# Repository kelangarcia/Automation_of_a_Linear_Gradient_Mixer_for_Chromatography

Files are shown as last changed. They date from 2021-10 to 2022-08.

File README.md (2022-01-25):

# Automation-of-a-Linear-Gradient-Mixer-for-Chromatography

This repository has all the files and documentation (3D Case, Code, Circuit Analysis, Circuit Simulations, Procedure, Schematics,Results etc.) that were used to create a machine that automates the process of mixing gradients for chromatography. A so called Gradient Mixer Machine.

All the folders and files included are explained below:

- "Automation of Gradient Mixer for Chromatography.pdf": Technical motivation and explanation of the machine. Includes explanation of the final design, circuit, code, etc... works.

- "3D Case": This folder includes the 3D files exported into .stl (This is the format used for 3D printing). Just upload this file to a 3D printer or sent it to a production company.

- "Circuit": It includes the "Circuit_Diagram.pdf" file, this is supporting material for when you are soldering the components. It is a good guide. It also includes the Datasheets for the most important hardware components used. Like the solenoid valve, and transistor.

- "Code": This folder includes three important files. Two gradient mixer codes and a zip file with the needed libraries. The zip file needs to be installed into your Arduino IDE (read the instruction set for more), once it is installed. You can upload one of the two Gradient Mixer code provided. First try with the original code and test the machine. If you notice that when there is a press in the touch screen it detects the touch but in the inverted y-axis position, then upload the second code (LCD inverted code).

- "Instruction Sets": Two .pdf files, one is the instructions for the user, and the other has the instructions for making the gradient mixer.

- "PCB": Includes the .fzz file for editing the PCB design, and it also includes the export files of the pcb in three diferent formats (.pdf, .svg, Gerber Files). Depending on the company you are printing the PCB with, they will request for the type of file. The most common is the Gerber File. The file "KGGradient_Mixer_06072021.zip" has all the Gerber Files compressed into a zip folder, you can send this zip file to the production company, or create your own zip file with the provided Gerber files.
 
- "EXTRA": Extra material

- "Gradient Mixer Price": List of materials with their average price inthe market, giving how much does this gradient mixer construction cost.

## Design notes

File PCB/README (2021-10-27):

Printing PCB

The export files of the PCB are in the folder "Production_Files". In there, all files are given in the most important formats.
In .pdf, .svg, and gerber file (the most important).
For PCB production, normaly gerber files are used. Just download all the gerber files, zip them together to one file and send it to the production company.
(Or just send the .zip file included with the name "KGGradient_Mixer_06072021.zip" which is located on the folder "Production File", which is a zip file containing the gerber files)

If you want to modify the PCB design, the file is also included with the name "Gradient_Mixer_05.07.2021.fzz" to edit this file you need the software fritzing.

When the pcb is ready, you need to solder all the components into the PCB, the circuit diagram showing which components to solder exactly where is on the pdf with the name
"Circuit_Diagram.pdf" on the folder name "Circuit"

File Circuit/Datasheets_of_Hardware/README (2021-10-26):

Datasheets of the transistor used (NPN TIP 120 Darlington Transistor) and the Solenoid valve used (Delays where taken into consideration).

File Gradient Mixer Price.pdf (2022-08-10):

Utility | Component | Price
Materials | 3.2" TFT LCD Display Touchscreen | € 15.24
| 3.2" TFT LCD Mega Shield V2.2 | € 12.39
| Arduino Mega 2560 | € 35.00
| TIP 120 Darlington Transistor | € 0.30
| 1N4001 Diodes 1A 50V | € 1.29
| Led's, Resistors, Interrupt Buttons,
| pins | € 7.99
| Long Arduino Pins | € 1.00
| 433MHz Wireless
| Transmitter/Receiver | € 1.90
| 433Mhz Wireless Power Socket | € 17.90
| 12V Power Supply | € 10.99
| Connectors | € 11.75
| 22AWG Electric Wire | € 8.99
| 1.5mm screws | € 1.00
| Printed 3D case | € 37.00
| Printed Circuit Board | € 34.00
| Solenoid Valve | € 150.00
| GPIO Cable 40 Pin Male to Female | € 21.00
| Extra High Female Pin Headers | € 10.00
| SubTotal | € 377.74
Equipment | Solder | € 10.00
| Tin | € 5.00
| Multimeter | € 5.00
| SubTotal | € 20.00
| Total | € 397.74

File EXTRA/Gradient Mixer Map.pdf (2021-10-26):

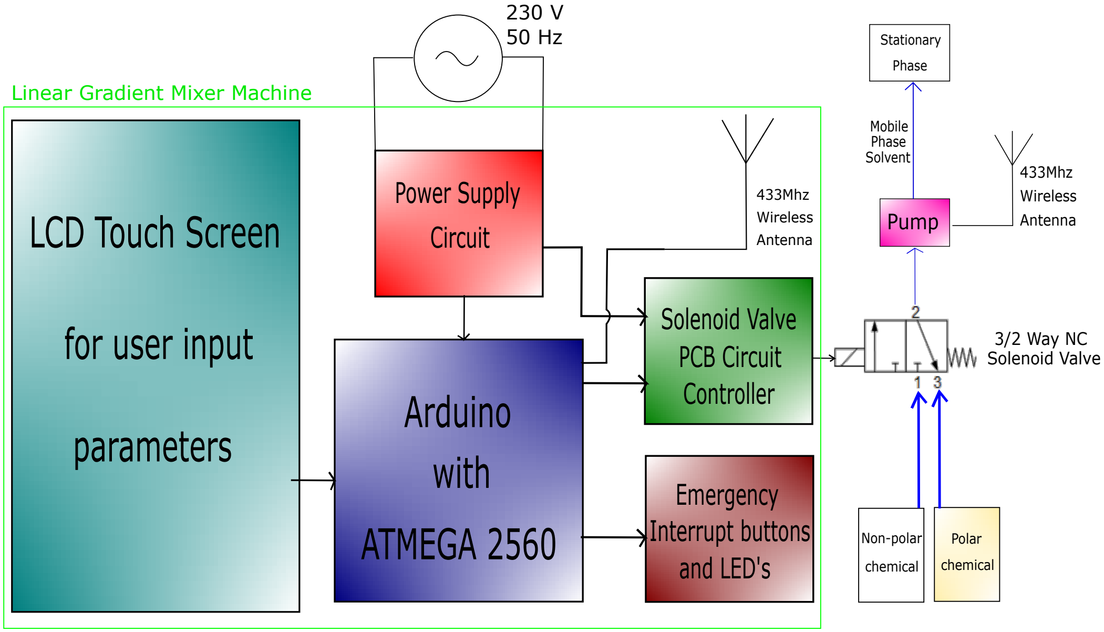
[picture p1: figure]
Arduino with ATMEGA 2560; PCB Circuit; Solenoid Valve; Emergency Interrupt buttons and LED's; LCD Touch Screen; for user input; Power Supply Circuit; parameters; 433Mhz Wireless Antenna; 3/2 Way NC Solenoid Valve; Non-polar; chemical; Polar; 433Mhz Wireless; Pump; Antenna; Mobile Phase Solvent; Stationary; Phase; Linear Gradient Mixer Machine; Controller

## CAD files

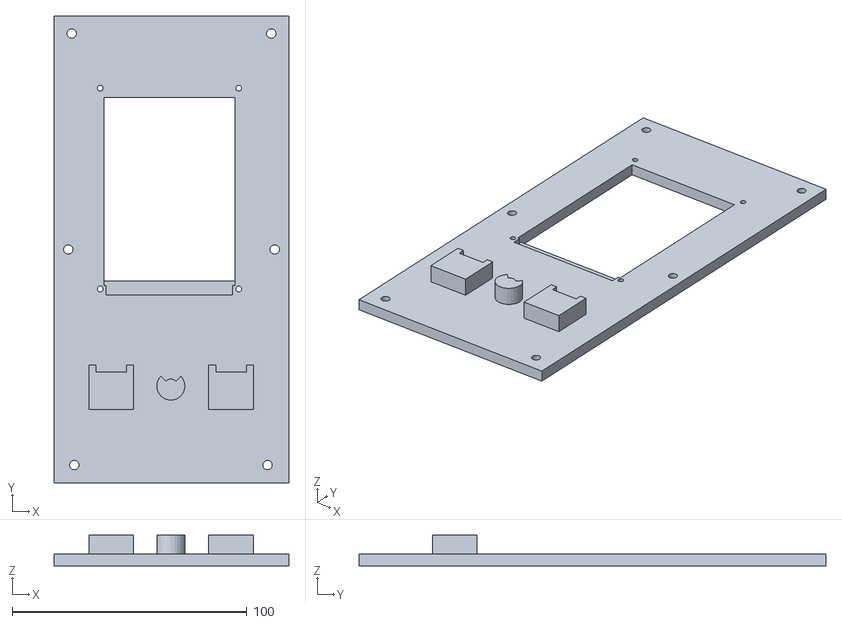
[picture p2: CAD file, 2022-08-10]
3D Case/Lid.stl
100.0 x 199.0 x 13.0

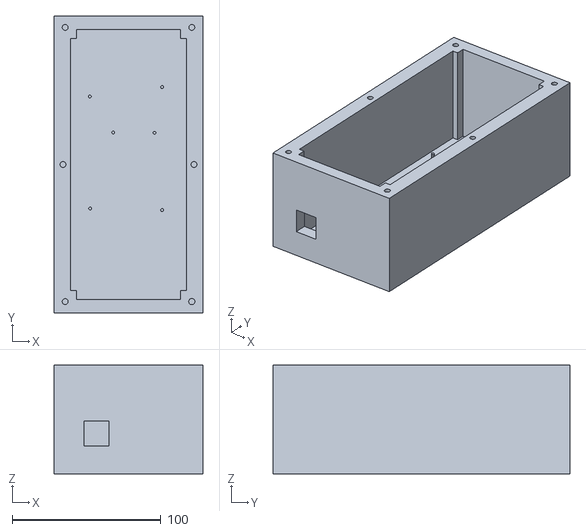
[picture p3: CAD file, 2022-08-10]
3D Case/Base.stl
100.0 x 199.0 x 73.0

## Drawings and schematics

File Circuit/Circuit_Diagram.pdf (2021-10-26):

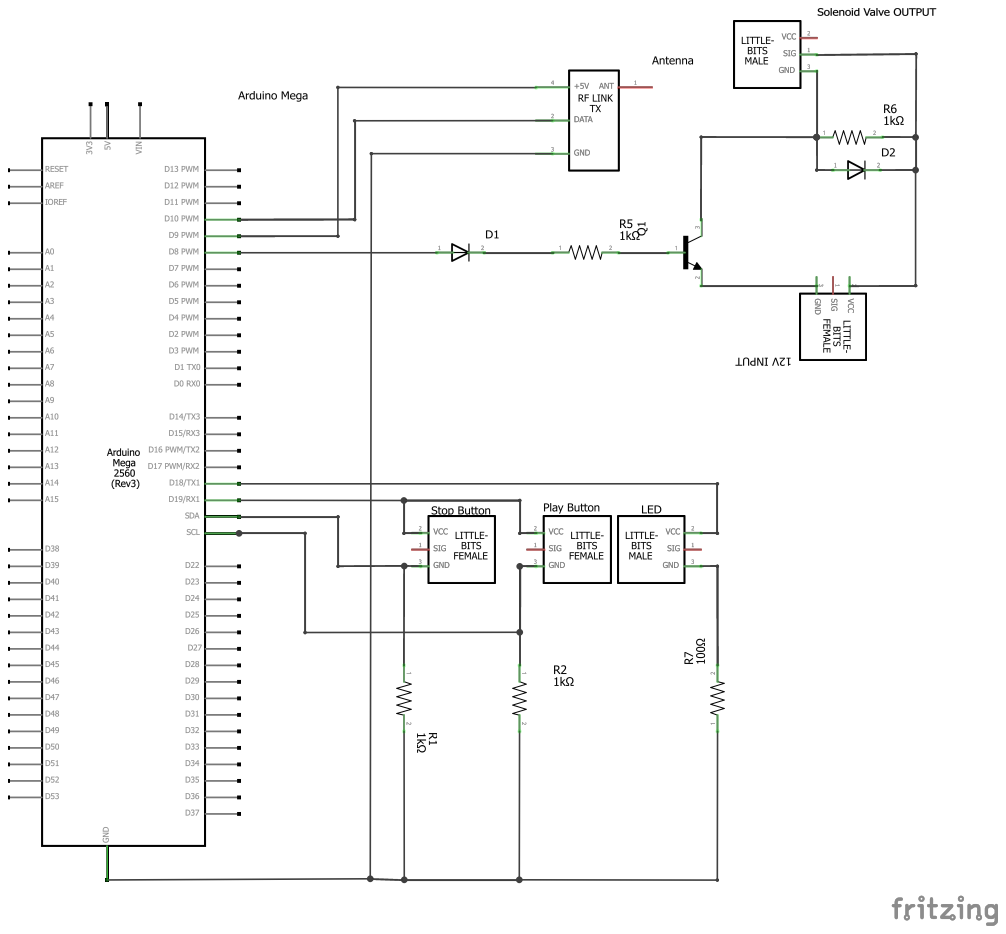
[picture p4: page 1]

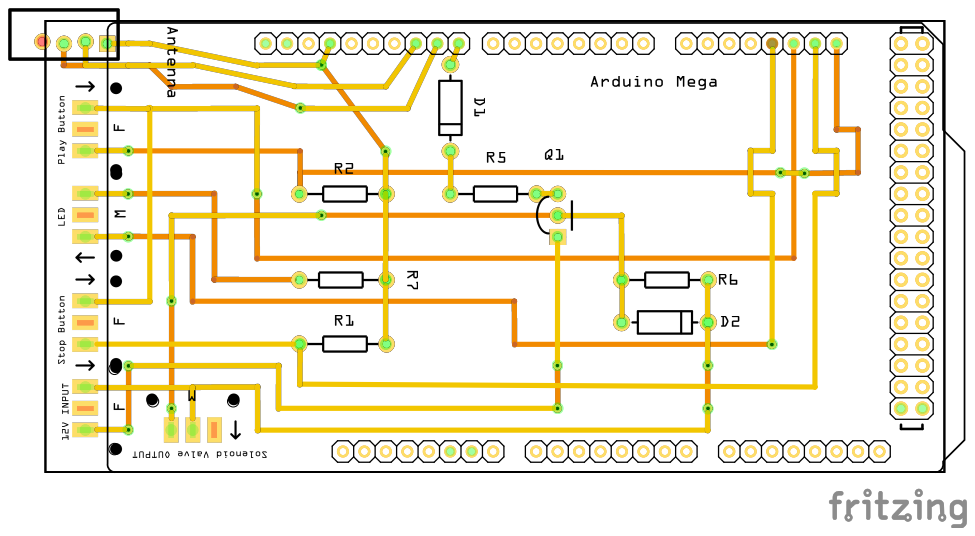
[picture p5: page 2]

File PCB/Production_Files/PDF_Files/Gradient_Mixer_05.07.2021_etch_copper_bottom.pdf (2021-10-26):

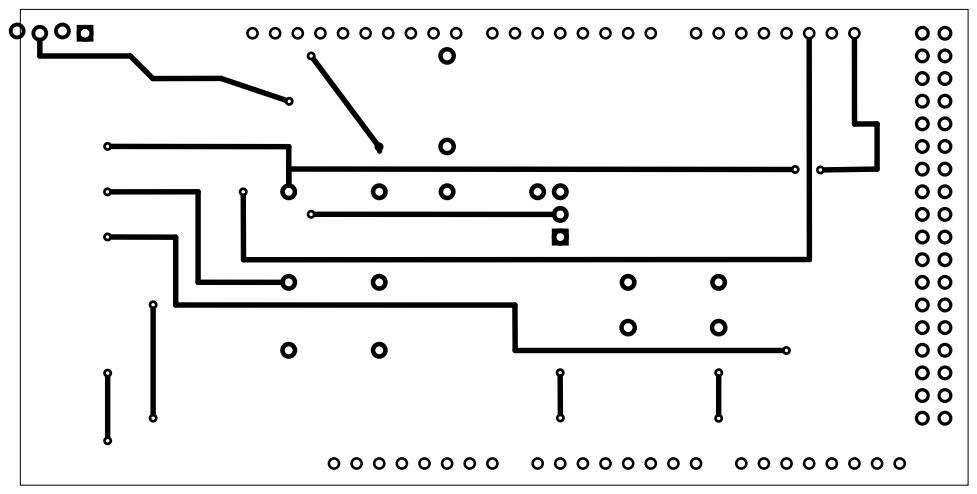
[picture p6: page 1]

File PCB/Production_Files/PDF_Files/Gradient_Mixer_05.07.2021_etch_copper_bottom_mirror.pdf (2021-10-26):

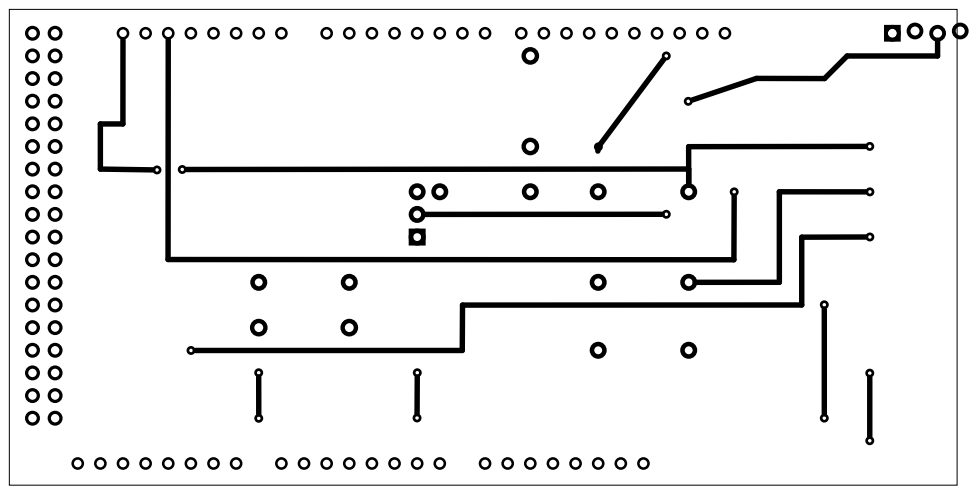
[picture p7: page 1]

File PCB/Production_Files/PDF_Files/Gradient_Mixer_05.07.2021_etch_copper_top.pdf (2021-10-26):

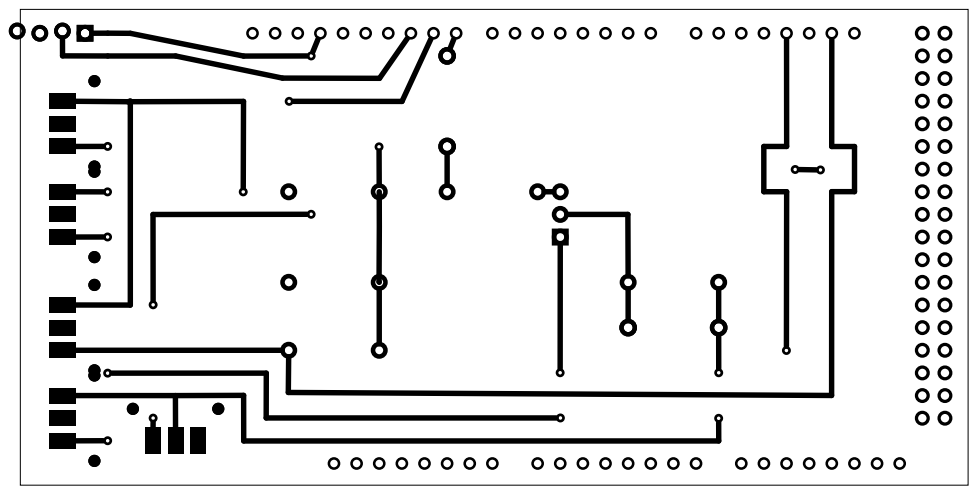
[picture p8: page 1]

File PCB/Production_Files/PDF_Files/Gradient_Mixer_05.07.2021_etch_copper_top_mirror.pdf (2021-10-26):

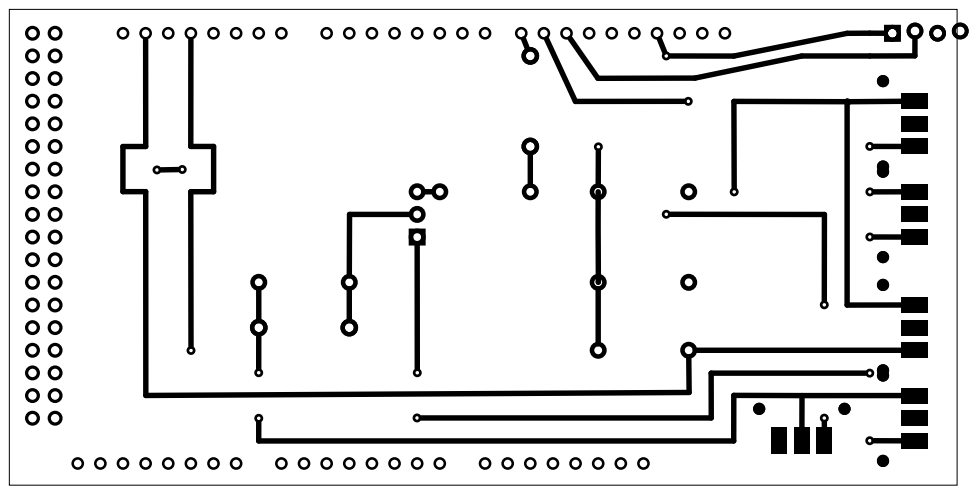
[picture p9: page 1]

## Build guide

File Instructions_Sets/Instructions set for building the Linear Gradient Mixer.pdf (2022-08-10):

Instructions set for building the Linear Gradient Mixer.

Procedure:
1. Open the GitHub Link for all the files and documentation needed.
2. Open the folder “3D Case” download both .stl files and send them to production.

### 3. Open the folder “PCB/Production_Files”. If the company printing the PCB

request for the Gerber files in a zip file, then download the document “KGGradient_Mixer_06072021.zip” and send it for production. Otherwise, if the company request for the .pdf or .svg files then download the needed folder, zip it and send it. Those folders are in “PCB/Production_Files”
- If you want to edit the PCB, the .fzz file is included so you can edit it.

### 4. Once you have the PCB, start soldering the components into the PCB. You can

follow the Circuit Diagram for a guide on where to solder the components. The file is on the folder “Circuit” under the name “Circuit_Diagram.pdf” Please use this documentation as reference when soldering the components.

### 5. Tips when soldering:

- Note: Using Female input pins is not mandatory but helps to swap components quickly. Attach female pins where the TFT pins will connect. Refer to schematic and see green connections as reference.
- Note that the PCB includes the name and numbering for the component. R5 means resistor 5, D1 diode 1, Q1 transistor 1 and so on.
- Note that the positive part of the 12V input should be connected to the cathode part of the diode.
- For the solenoid valve output, the polarity does not matter but, it is better to consider the transistor part as negative and the positive 12V part as positive.
- The 12V power supply can be connected in parallel to the Arduino and in parallel to the PCB circuit. In this way we only use one 12V power supply and not two. i.e.: 12V
Arduino Mega
2560

PCB
Circuit

- Remember that the PCB will be top mounted to the Arduino Mega2560. Therefore, do not forget to solder the short pins into the PCB. Use short pins only to the PCB connections that are used in the Arduino. Which are:
o pins Gnd,8,9,10,18,19,20,21
- Solder the antenna transmitter to the PCB. Make sure you leave space for the top-mounted 3,2” LCD Touch Screen with the TFT Shield.
- Insert the 3,2” LCD Touch Screen into the TFT Shield. Then, top mount the whole thing into the PCB. At the button part of the PCB solder the shield pins with the extended pins. After soldering the Shield pins with the extended pins, cut all the pins so they are at the same height as the short pins from the PCB.
- Solder one side of the cables to the peripherals (Buttons and LED) and the other side solder it to the PCB, so you have room to move them and place them in their spot.
6. Download Arduino IDE.
7. Install needed libraries into Arduino IDE.
- Download the “Needed Libraries” folder which is located in “Code/Needed Libraries"
- Unzip the file, three folders will appear. Each folder is a library.
- Move the three folders into a desire location, make sure to remember the path.
- Open Arduino IDE, go to the “sketch” tap on the top left part.
- Go to “Include Library” and then to “Add .ZIP Library…” and then select one folder out of the three and then done.
- Repeat the last two steps to include the other two folders’ libraries.
- Restart the Arduino IDE

### 8. Now you are ready to mount the whole circuit to the Arduino Mega, but before

that we need to find the binary on and off code, pulse length and protocol of your 433Mhz Power Outlet.

- To find the needed parameters to control your 433MHz Power Outlet you need to connect an 433MHz RF receiver to Digital Pin 2 of your Arduino.

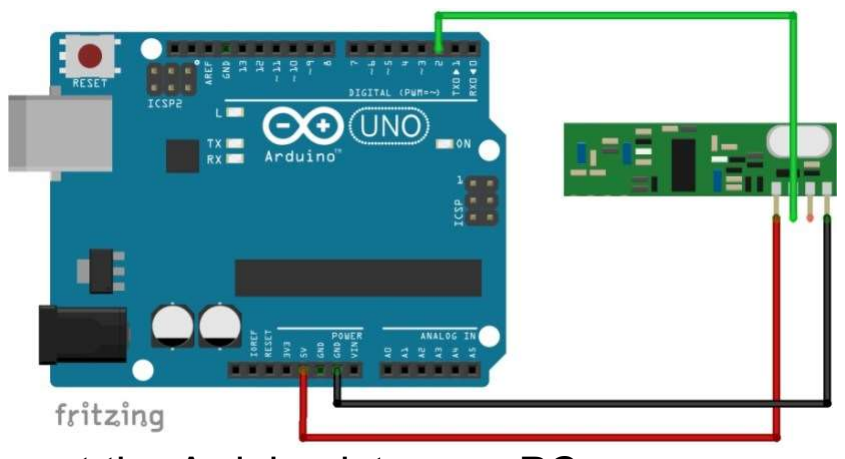
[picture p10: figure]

- Connect the Arduino into your PC.
- Go to “tools” -> “Board” select Arduino Mega2560.
- Go to “tools” -> “Processor” select ATMega2560
- Go to “tools” -> “Port” select the Arduino port it may be as COMXX where XX is a number
o You can get the number of the COM port under the device manager part of windows.
- Go | to | “Files” | -> | “Examples…” | -> | “rc-switch” | ->
“Received_demo_Advanced”. A new tap with a code will appear
- Press the upload button.
- Now, the Arduino is receiving and reading all the signals at the 433Mhz frequency. To see the signal code and protocols. Open the Arduino IDE serial monitor.
- Once you have the serial monitor open, the Arduino will display all the signal properties. Grab your 433Mhz RF remote control and turn on the power outlet. Once you did that, you will notice that two code lines appeared at the screen.
- From these code lines record the Binary code, Pulse Length, and Protocol number for turning the outlet on.
- Repeat the last two steps but this time by turning the outlet off.
- Once you have recorded all three values for on and three for off you can unplug the Arduino from your PC and disassemble the whole circuit.

9. Adapting the code.
- Download the Gradient Mixer code the file name is “Original_Code.ino” first download it from “Code/Original Code/Original_Code.ino”
- Open the file and go to the section of declaration of global variables.
- Below the comment ”//Antenna Communication Code” is the code line that sets “const int pulse length = 718;” change the number 714 to your recorded Pulse Length.
- Also, change the parameters for the protocol and for the binary code. The code line for the protocol is “const int protocol = 2” and for the antenna binary code to turn it on is “const char* antennaOn = “10100110000010000101111000000000” ”
- Also change the code for antennaOff
- If you want to change the time limit, which currently is 360 min. Go to the void setup(){} function and please look for the comment
/*

You can change the restrictions in here (in the if statement)!! To Change time limit, change the inequality value for "time2<=360"
meaning that 360 it is the maximum allowed minutes time.

*/”
And change the 360 value to the desire value in the if statement.

### 10. After adapting the code, we are done with all editing part and now we are just

missing to test it and assemble the final product. Please top mount the Solder PCB with the touch screen and the shield to the Arduino Mega 2560.

### 11. Connect the Arduino Mega 2560 to your PC, check that the values of “tools” -

> “Board”; “tools” -> “Processor”; and “tools” -> “Port” are the correct ones. (See step 8 for reference)

### 12. Press the upload button and wait until all the code has been uploaded to the

Arduino.

### 13. Test the LCD touch screen. If screen detects the touch in the same x-axis but

in the inverted y-axis. Then repeat step 9 but with the code

“LCD_Inverted_Code.ino” from “Code/LCD_Inverted_Code/” and not from “Code/Original Code/”.

### 14. Once the Touch Screen works perfectly. Go ahead and assemble the gradient

mixer with the 3D case by attaching the shield and display with the GPIO ribbon cable.

### 15. Tips for assembling the final product

- Use the female power connector pins and place them in the circular part of the case.
- Use the six screws to hold everything in place.
- Solder one part of the cable to the PCB ports and the other side of the cables to the power female adapters. In the male power adapters to connect to the gradient mixer from the outside. The power connectors should be for the solenoid valve and for the 12V power input.
- Use the USB2.0B extension to connect the Arduino and to connect the other part of the extension in square that is on the left side of the case.
16. Enjoy your Gradient Mixer.

### 17. For more information read the README files on the GitHub link for more

information while doing the Gradient Mixer.

Materials: Printed Circuit Board (PCB) (files provided)

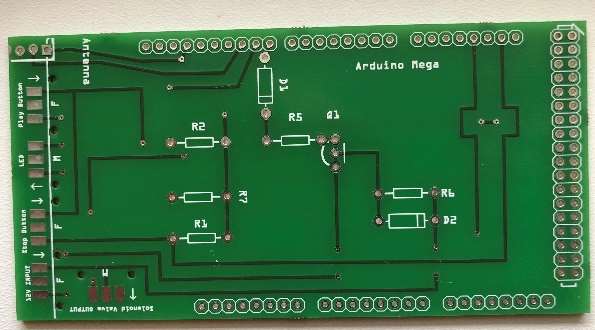
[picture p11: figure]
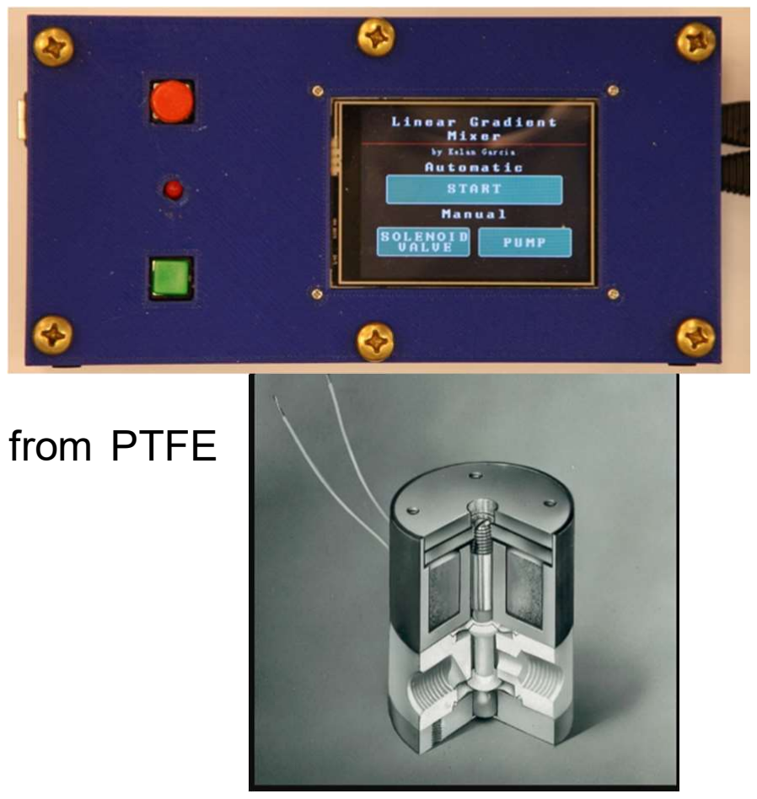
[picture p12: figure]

- Printed 3D Case (files provided) 12V 3/2-Way Mini Solenoid Valve made from PTFE

(Reichelt Chemietechnik)

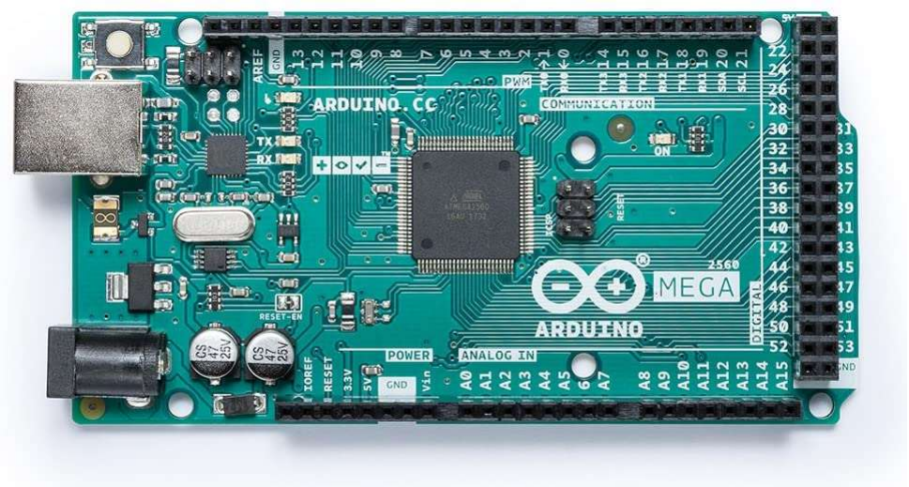
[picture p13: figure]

- Arduino Mega 2560

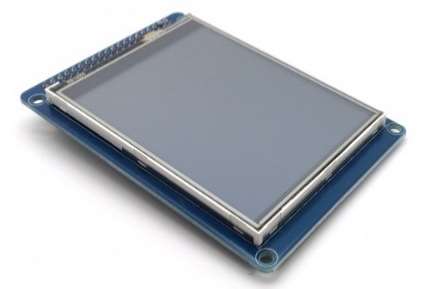
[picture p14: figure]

- AptoFun 3.2" TFT LCD Touchscreen

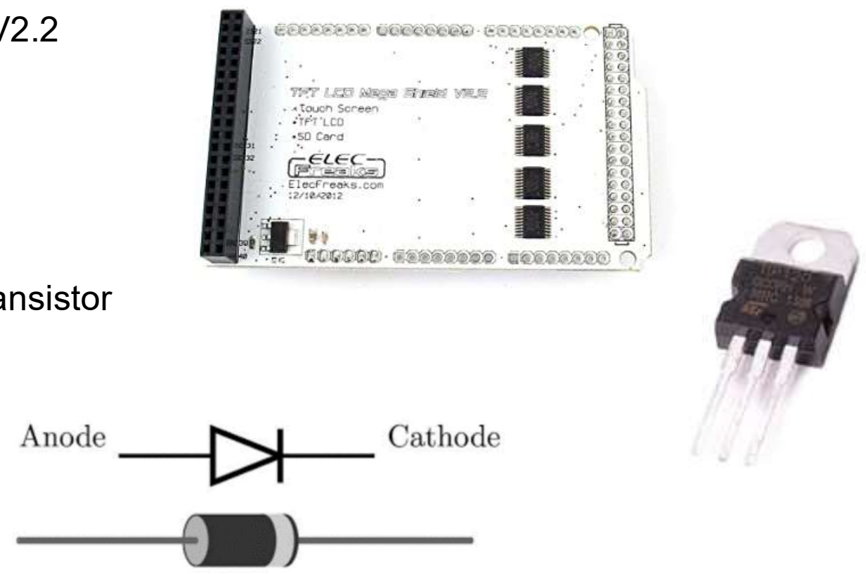
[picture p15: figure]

- TFT 3,2 LCD Mega Shield V2.2 NPN TIP 120 Darlington Transistor Two 1N4001 diodes. 433Mhz | transmitter | and

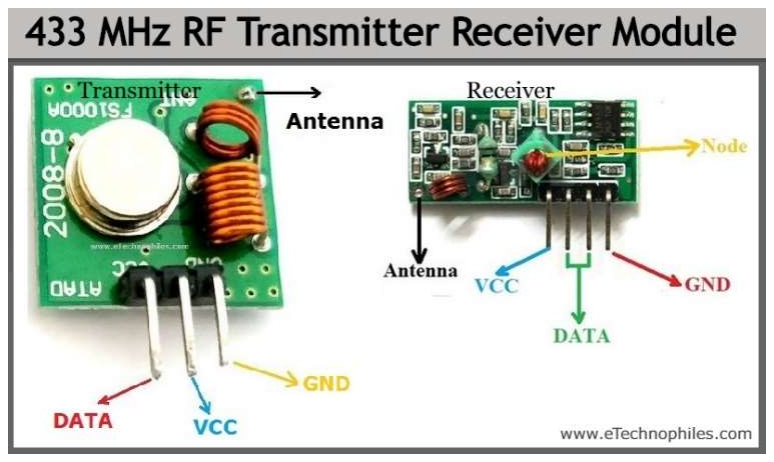
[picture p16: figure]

receiver for Arduino’s.

- Power connectors adapters

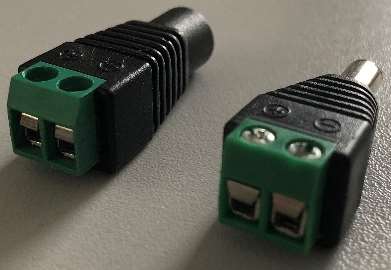
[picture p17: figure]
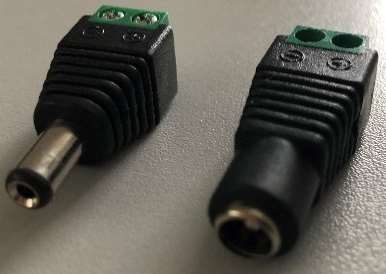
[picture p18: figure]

- Extra Long Connector Arduino Pins and normal connector pins

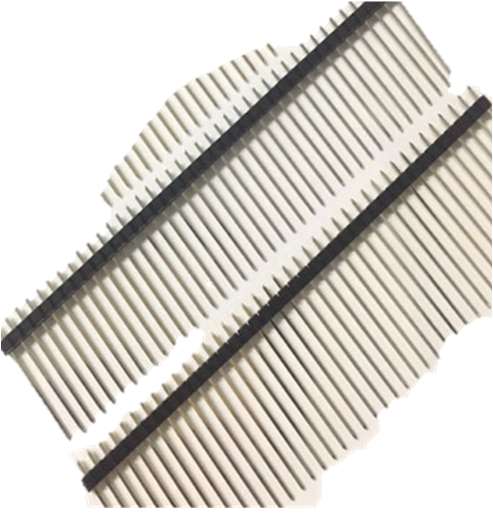
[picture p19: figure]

- GPIO Cable 40 Pin Male to Female

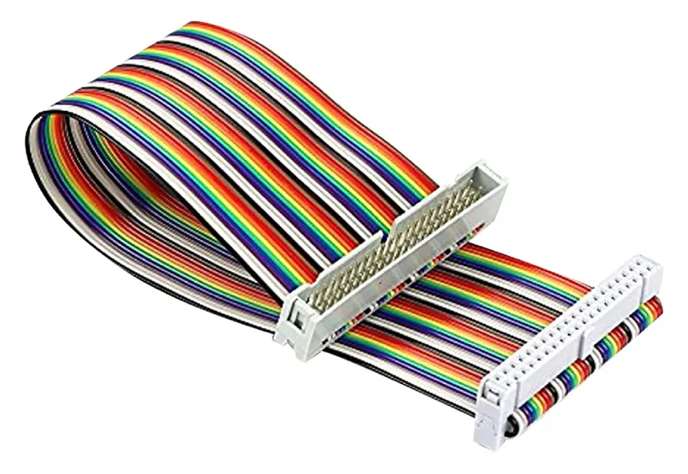
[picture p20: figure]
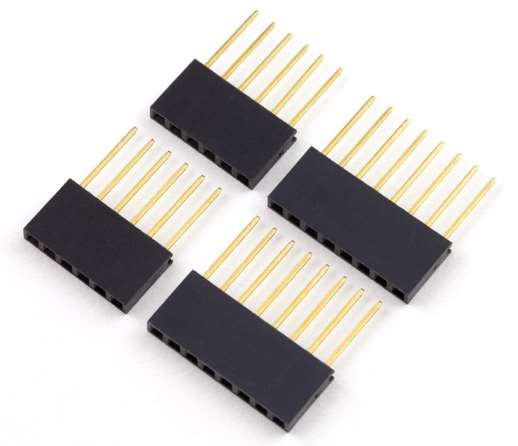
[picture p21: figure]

- Extra High Female pin headers one 1x8, one 1x6, one 2x18, five 1x3
- Cables
- Four 1kΩ resistors and one 100Ω resistor
- LEDs
- Push Buttons
- Soldering Station and Tin wire
- 12V Power supply
- 6 Screws and a screwdriver
- USB 2.0B short extension
- Multimeter for testing

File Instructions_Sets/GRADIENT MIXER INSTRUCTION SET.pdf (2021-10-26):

GRADIENT MIXER INSTRUCTION SET

Homepage

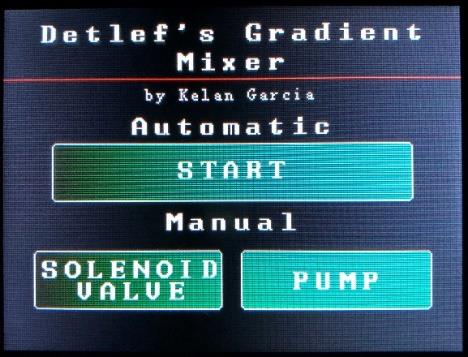
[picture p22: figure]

- There are two ways to control the gradient mixer, an automatic

way and a manual way.

- The Automatic way is the “START” green button.
- The Manual Way controls two components, the solenoid valve

and the pump. Both buttons redirects you to a new page where

you can control each state.

Manual Way

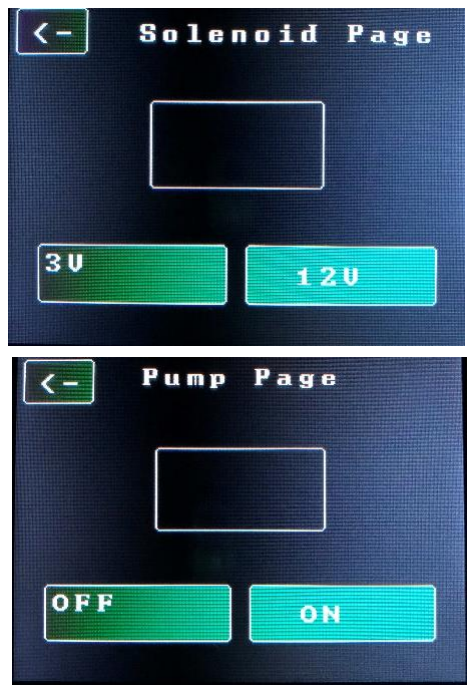
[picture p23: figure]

- To manually control the state of the valve, enter the solenoid

valve page. Two buttons and one rectangle will appear, the “3V”

button sets the solenoid valve in the off state and the “12V”

button sets it to the on state. The rectangle in the middle will be

yellow or black, if it is in yellow it indicated that the valve is on

the on state, and if it is black then it is on the off state.

- The pump can be turn on and off manually on the pump page.

The square in in the middle works the same as in the solenoid

page. Black means off and yellow means on.

Automatic Way

- The automatic way creates a linear gradient depending on the

four inserted values.

- The gradient mixer will maintain the initial percentage inserted

in %T1 for T1minutes.

- After T1minutes, the percentage will start to linearly increase

until it reaches the percentage inserted in %T2 and it will take

T2 minutes.

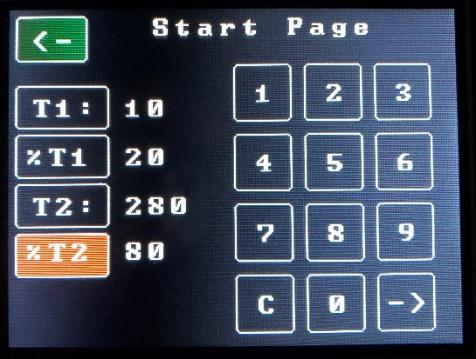
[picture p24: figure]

- The maximum time the gradient mixer can run is 6 hours. Therefore, 360 minutes is the max number

for T2.

- Other restrictions are:1 < T1 ≤ 10; %T1 ≥ 1; T1 < T2; %T1 < %T2 ≤ 100, #This restrictions can

be change on the arduino code.

- When enter is pressed, the gradient mixer will show a preview of the graph that it’s going to follow.

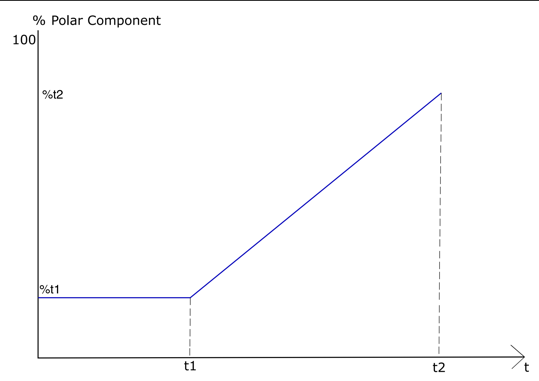
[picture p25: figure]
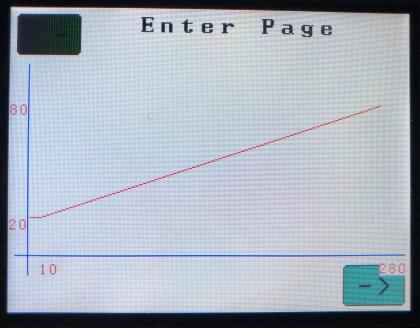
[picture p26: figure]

- Make sure that when the solenoid valve is on the on state (12V), the chemical flowing is the Polar one

(or the chemical increasing).

- After confirming the preview graph, it will redirect you to the process page. In this page all the process

starts automatically, it starts with the polar solvent flowing and then the non-polar. Once in the process

page you cannot go back unless the progress has finished. The only way to stop the process is by using

the emergency button and it will turn everything off. This page also updates you with all the progress

of the mixer. It will indicate in which step of the process is in, either (0,t1] or (t1,t2]. It will also show

how many cycles per step are needed, in which cycle it’s on, it shows which chemical is flowing by

filling its corresponding square in yellow and it shows by how many milliseconds it will flow.

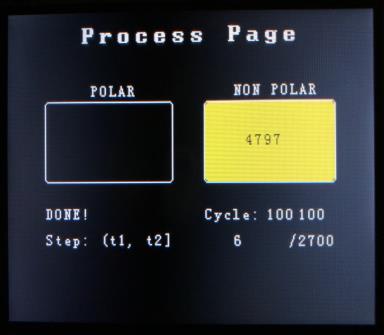
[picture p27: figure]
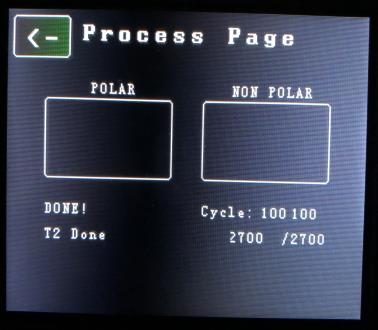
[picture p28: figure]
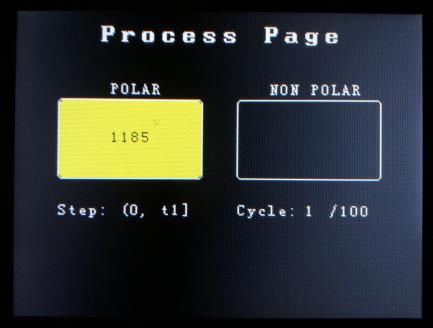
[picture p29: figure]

- Each cycle last 6 seconds,. So, if its missing 1,000 cycles for it to finish. It will take

1,000 × 6 seconds ∙

1 min
60 seconds

=

1,000 min
10

= 100 minutes.

Emergency Stop Buttons

- The stop buttons only work when the gradient mixer is on the process page of the automatic part. If

the gradient mixer is on another page, then all button press are ignored.

- Red button is to stop the automatic process at any moment. The process will stop from where it was,

it will wirelessly turn the pump off and it will turn on the red LED indicating that the process is on

hold.

- To renew the process from where it was, press and hold for 1 second two times the green button. This will wirelessly turn the pump on, turn off the LED, and it will container the gradient mixer from where it was stopped.

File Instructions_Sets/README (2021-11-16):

Here, you find two files.

One file is the instructions for the user(GRADIENT MIXER INSTRUCTION SET.pdf), and the other are the instrcutions for making the Gradient Mixer machine(Instructions set for building the Linear Gradient Mixer.pdf).

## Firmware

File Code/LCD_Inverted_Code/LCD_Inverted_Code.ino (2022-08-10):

// Libraries needed for the Touch LCD and RF transmitter
#include <UTFT.h>
#include <URTouch.h>
#include <RCSwitch.h>
#include <math.h>
#include <stdlib.h>

// Initializing the LCD, Touch Screen and RF Transmitter
UTFT    myGLCD(ILI9341_16,38,39,40,41); //LCD models and pins
URTouch  myTouch(6, 5, 4, 3, 2); // Touch pins
RCSwitch mySwitch = RCSwitch(); //RF Transmitter

// Pins for externals tools
const int VALVE = 8;
const int VCC = 9;
const int Antenna = 10;

//Needed variables
extern uint8_t SmallFont[];
extern uint8_t BigFont[];
extern uint8_t SevenSegNumFont[];

int x, y; //x and y position of the user input via the touch screen
char currentPage, selectedUnit; //Page Position
int pump = 0;
int valve = 0;

int RT1 = 0;
int RT2 = 0;
int RA = 0;
int RB = 0;


char T1[4] = "";
char A[4] = "";
char T2[4] = "";
char B[4] = "";


int stCurrentLen1=0;
int stCurrentLen2=0;
int stCurrentLen3=0;
int stCurrentLen4=0;

int time1 = 0;
int percentageA = 0;
int time2 = 0;
int percentageB = 0;
int once = 0;
char buffer [33];

//Antena Communication Code

const char* antennaOn = "10100110000010000101111000000000";
const char* antennaOff = "10101110000010000101111000000000";

const int pulse_length = 718;
const int protocol = 2;
const int repeat_transmit = 2;

// Pins for Stop Buttons
const int StopLED = 18;
const int ButtonsVcc =19;
const int StopButton = 20;
const int PlayButton = 21;

// variables will change:
int buttonState = 0;         // variable for reading the pushbutton status

unsigned long LastInterrupt; //Checking time passed in ISR vector 

void setup() {
  // Initial setup
  Serial.begin(9600);

  // Given 5V to the VCC(power) pin
  pinMode(VCC, OUTPUT);
  digitalWrite(VCC, HIGH);
  
  // Declaring that the valve pin is an output
  pinMode(VALVE, OUTPUT);
  
  // Transmitter is connected to Arduino Pin #10  
  mySwitch.enableTransmit(Antenna);

  // Optional set pulse length.
  mySwitch.setPulseLength(pulse_length);
  
  // Optional set protocol (default is 1, will work for most outlets)
  mySwitch.setProtocol(protocol);

  // Optional set number of transmission repetitions.
  mySwitch.setRepeatTransmit(repeat_transmit);
  
  //turning the valve off
  digitalWrite(VALVE, LOW);
  //Change Binary Code to your own binary code for turning the pump off
  mySwitch.send(antennaOff);

  // Initializing and clearing the screen
  myGLCD.InitLCD();
  myGLCD.clrScr();

  myTouch.InitTouch();
  myTouch.setPrecision(PREC_EXTREME);

  //Font and Backcolor
  myGLCD.setFont(BigFont);
  myGLCD.setBackColor(0, 0, 255);

  // StopButton PINS USED
  pinMode(ButtonsVcc, OUTPUT);
  digitalWrite(ButtonsVcc, HIGH);
  pinMode(StopLED, OUTPUT);
  pinMode(StopButton,INPUT);
  pinMode(PlayButton, INPUT);
  
  // Attach an interrupt to the ISR vector
  attachInterrupt(digitalPinToInterrupt(StopButton), PauseProgram,  RISING);

  Mainmenu();
  currentPage = '0'; 
}

void loop(){
  //if (myTouch.dataAvailable()){
  //  myTouch.read();
  //  x=myTouch.getX();
  //  y=myTouch.getY();
      
    if (currentPage == '0'){ // Main Page
      if (myTouch.dataAvailable()){
        myTouch.read();
        x=myTouch.getX();
        y=myTouch.getY();
        if ((y >= 105) && (y <= 145) && (x >= 35) && (x <= 285)){
          waitForIt(35, 95, 285, 135);
          myGLCD.clrScr();
          startPage();
          currentPage = '1';
        }
        if ((y >= 30) && (y <= 70)){  // Manual 
          if ((x>=22) && (x<=153)){  // Button: Solenoid Valve
            waitForIt(22, 170, 153, 210);
            myGLCD.clrScr();
            solenoidPage();
            currentPage = '2';
          }
          if ((x>=167) && (x<=298)){  // Button: PUMP
            waitForIt(167, 170, 298, 210);
            myGLCD.clrScr();
            pumpPage();
            currentPage = '3';
          }
        }
      }
    }
    
    if (currentPage == '1'){ // Start Page
      if (myTouch.dataAvailable()){
        myTouch.read();
        x=myTouch.getX();
        y=myTouch.getY();
            
        //Back to Main Menu
        if ((y >= 203) && (y <= 235) && (x >= 5) && (x <=55)){
          waitForIt(5, 5, 55, 37);

          // Erasing inserted values
          T1[0] = '\0';
          stCurrentLen1 = 0;
          A[0] = '\0';
          stCurrentLen2 = 0;
          T2[0] = '\0';
          stCurrentLen3 = 0;
          B[0] = '\0';
          stCurrentLen4 = 0;

          // Drawing Main Menu Page
          myGLCD.clrScr();
          Mainmenu();
          currentPage = '0';
        }
        if((y >= 160) && (y <= 200)){
          if((x >= 160) && (x <= 200)){//1
            waitForIt(160, 40, 200, 80);
            if (RT1 == 1){
              updateStr('1',80,63,1);
            }
            else if(RA == 1){
              updateStr('1',80,98,2);
            }
            else if(RT2 == 1){
              updateStr('1',80,133,3);
            }
            else if(RB == 1){
              updateStr('1',80,165,4);
            }
          }
          if((x >= 210) && (x <= 250)){//2
            waitForIt(210, 40, 250, 80);
            if (RT1 == 1){
              updateStr('2',80,63,1);
            }
            else if(RA == 1){
              updateStr('2',80,98,2);
            }
            else if(RT2 == 1){
              updateStr('2',80,133,3);
            }
            else if(RB == 1){
              updateStr('2',80,165,4);
            }
          }
          if((x >= 260) && (x <= 300)){//3
            waitForIt(260, 40, 300, 80);
            if (RT1 == 1){
              updateStr('3',80,63,1);
            }
            else if(RA == 1){
              updateStr('3',80,98,2);
            }
            else if(RT2 == 1){
              updateStr('3',80,133,3);
            }
            else if(RB == 1){
              updateStr('3',80,165,4);
            }
          }
        }
        if((y >= 110) && (y <= 150)){
          if((x >= 160) && (x <= 200)){//4
            waitForIt(160, 90, 200, 130);
            if (RT1 == 1){
              updateStr('4',80,63,1);
            }
            else if(RA == 1){
              updateStr('4',80,98,2);
            }
            else if(RT2 == 1){
              updateStr('4',80,133,3);
            }
            else if(RB == 1){
              updateStr('4',80,165,4);
            }
          }
          if((x >= 210) && (x <= 250)){//5
            waitForIt(210, 90, 250, 130);
            if (RT1 == 1){
              updateStr('5',80,63,1);
            }
            else if(RA == 1){
              updateStr('5',80,98,2);
            }
            else if(RT2 == 1){
              updateStr('5',80,133,3);
            }
            else if(RB == 1){
              updateStr('5',80,165,4);
            }
          }
          if((x >= 260) && (x <= 300)){//6
            waitForIt(260, 90, 300, 130);
            if (RT1 == 1){
              updateStr('6',80,63,1);
            }
            else if(RA == 1){
              updateStr('6',80,98,2);
            }
            else if(RT2 == 1){
              updateStr('6',80,133,3);
            }
            else if(RB == 1){
              updateStr('6',80,165,4);
            }
          }
        }
        if((y >= 60) && (y <= 100)){
          if((x >= 160) && (x <= 200)){//7
            waitForIt(160, 140, 200, 180);
            if (RT1 == 1){
              updateStr('7',80,63,1);
            }
            else if(RA == 1){
              updateStr('7',80,98,2);
            }
            else if(RT2 == 1){
              updateStr('7',80,133,3);
            }
            else if(RB == 1){
              updateStr('7',80,165,4);
            }
          }
          if((x >= 210) && (x <= 250)){//8
            waitForIt(210, 140, 250, 180);
            if (RT1 == 1){
              updateStr('8',80,63,1);
            }
            else if(RA == 1){
              updateStr('8',80,98,2);
            }
            else if(RT2 == 1){
              updateStr('8',80,133,3);
            }
            else if(RB == 1){
              updateStr('8',80,165,4);
            }
          }
          if((x >= 260) && (x <= 300)){//9
            waitForIt(260, 140, 300, 180);
            if (RT1 == 1){
              updateStr('9',80,63,1);
            }
            else if(RA == 1){
              updateStr('9',80,98,2);
            }
            else if(RT2 == 1){
              updateStr('9',80,133,3);
            }
            else if(RB == 1){
              updateStr('9',80,165,4);
            }
          }
        }
        if((y >= 10) && (y <= 50)){
          if((x >= 160) && (x <= 200)){//C
            waitForIt(160, 190, 200, 230);
            if (RT1 == 1){
              T1[0] = '\0';
              stCurrentLen1 = 0;
              myGLCD.setColor(0, 0, 0);
              myGLCD.fillRect(80, 63, 150, 93);
            }
            else if(RA == 1){
              A[0] = '\0';
              stCurrentLen2 = 0;
              myGLCD.setColor(0, 0, 0);
              myGLCD.fillRect(80, 98, 150, 128);
            }
            else if(RT2 == 1){
              T2[0] = '\0';
              stCurrentLen3 = 0;
              myGLCD.setColor(0, 0, 0);
              myGLCD.fillRect(80, 133, 150, 163);
            }
            else if(RB == 1){
              B[0] = '\0';
              stCurrentLen4 = 0;
              myGLCD.setColor(0, 0, 0);
              myGLCD.fillRect(80, 165, 150, 195);
            } 
          }
          if((x >= 210) && (x <= 250)){//0
            waitForIt(210, 190, 250, 230);
            if (RT1 == 1){
              updateStr('0',80,63,1);
            }
            else if(RA == 1){
              updateStr('0',80,98,2);
            }
            else if(RT2 == 1){
              updateStr('0',80,133,3);
            }
            else if(RB == 1){
              updateStr('0',80,165,4);
            }
          }
          if((x >= 260) && (x <= 300)){//->
            waitForIt(260, 190, 300, 230);
            if ((stCurrentLen1 != 0) && (stCurrentLen2 != 0) && (stCurrentLen3 != 0) && (stCurrentLen4 != 0)){
              
              // Converting Strings to INT    
              time1 = convertarraytoint(T1,stCurrentLen1);
              percentageA = convertarraytoint(A,stCurrentLen2);
              time2 = convertarraytoint(T2,stCurrentLen3);
              percentageB = convertarraytoint(B,stCurrentLen4);
              
              /*
               You can change the restrictions in here (in the if statement)!!
               To Change time limit, change the inequality value for "time2 <= 360"
               meaning that 360 its the maximum allowed minutes time.
              */
              if ((time1 >= 0) && (time2 > time1) && (time2 <= 360) && (percentageA >= 1) && (percentageB > percentageA) && (percentageB <= 100)){ // Checks if the inputs are correct
                myGLCD.clrScr();
                EnterPage();
                currentPage = '4';
              }
              else{

                myGLCD.setBackColor(0,0,0); // Sets the background color of the area where the text will be printed to black
                myGLCD.setColor(255, 0, 0); // Sets color to white
                myGLCD.setFont(BigFont); // Sets font to big
                myGLCD.print("Incorrect Input!", 60, 5);

                delay(500);

                myGLCD.setBackColor(0,0,0);
                myGLCD.setColor(0,0,0); // Sets the background color of the area where the text will be printed to black
                myGLCD.fillRoundRect(60, 0, 319, 25);

                delay(500);
                
                myGLCD.setColor(255, 0, 0); // Sets color to white
                myGLCD.print("Incorrect Input!", 60, 5);
                
                delay(1000);

                myGLCD.setBackColor(0,0,0);
                myGLCD.setColor(0,0,0); // Sets the background color of the area where the text will be printed to black
                myGLCD.fillRoundRect(60, 0, 319, 25);
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

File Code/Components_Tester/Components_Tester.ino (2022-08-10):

/*
 * With this code buttons, LED and transmitter can be tested. 
 */

#include <RCSwitch.h>
RCSwitch mySwitch = RCSwitch();

// Pins for Stop Buttons                                 
const int StopLED = 18;
const int ButtonsVcc =19;
const int StopButton = 20;
const int PlayButton = 21;

const int VALVE = 8;
int pump = 0;

//transmitter codes
const char* antennaOn = "10100110000010000101111000000000";
const char* antennaOff = "10101110000010000101111000000000";
unsigned long lastInterrupt;

// variables will change:
volatile int buttonState = 0;         // variable for reading the pushbutton status

void setup() {
  Serial.begin(9600);

  pinMode(9, OUTPUT);
  digitalWrite(9, HIGH); //POWER ANTENNA
  // Transmitter is connected to Arduino Pin #10  
  mySwitch.enableTransmit(10);

  // Optional set pulse length.
  mySwitch.setPulseLength(718);
  
  // Optional set protocol (default is 1, will work for most outlets)
  mySwitch.setProtocol(2);

  // Optional set number of transmission repetitions.
  mySwitch.setRepeatTransmit(2);

  //pinMode(12, OUTPUT);
  //
  digitalWrite(12, LOW); 
   pinMode(ButtonsVcc, OUTPUT);
  digitalWrite(ButtonsVcc, HIGH);

  pinMode(VALVE, OUTPUT);
  
  
  pinMode(StopLED, OUTPUT);
  
  pinMode(StopButton,INPUT);
  pinMode(PlayButton, INPUT);
  
  // Attach an interrupt to the ISR vector
  attachInterrupt(digitalPinToInterrupt(StopButton), PauseProgram,  RISING);
}

void loop() {
  // put your main code here, to run repeatedly:
  digitalWrite(VALVE, LOW);
  digitalWrite(StopLED, LOW);
  delay(5);
  digitalWrite(VALVE, HIGH);
  digitalWrite(StopLED, HIGH);
  delay(5);
}

void PauseProgram(){
  if(millis() - lastInterrupt > 10) // we set a 10ms no-interrupts window
    {    

      int decider = 1;
  
      pump = 0;
      //You can delete the codeline below if you dont want to turn off the pump when the program is paused
      mySwitch.send(antennaOff);//Change Binary Code to your own binary code for turning the pump off
      digitalWrite(StopLED, HIGH);
      
      //Wait until Play Button is pressed
      while(decider == 1){
        buttonState = digitalRead(PlayButton);
        if (buttonState > 0.1){
          decider = 0;
        }
      }
      
      //Turns Pump ON
      pump = 1;
      //You can delete the codeline below if you dont want to turn nf the pump when the program goes back to work
      mySwitch.send(antennaOn);//Change Binary Code to your own binary code for turning the pump on
      digitalWrite(StopLED, LOW);

      lastInterrupt = millis();
    }
}

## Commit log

2021-10-26 Create PCB
2021-10-26 Add files via upload
    Datasheet of the solenoid valve, anf the NPN TIP 120 Darlington Transistor
2021-10-26 Add files via upload
    Technical explanation of machine design, circuit, code, etc...
2022-03-21 Updated pin layout for new pcb
2022-03-21 Bug fix: interrupt button running twice. comment: This was a software fix but hardware fix with a capacitor on parralel with the button reload has to be implemented.
2022-03-21 Added necessary libraries and included debugging code to test the pcb.
2022-03-22 Non_updated local_files in Kelans Laptop
    [4xRod.stl, Lid.stl, Lower_Part.stl, Lowerpartbox 1.stl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]
2022-08-08 Improving case
    Made the case larger and more secure. Made larger to fit new ribbon cable for attaching display to lid. Added studs to help hold Arduino in place.
    [Base.stl, Lid.stl]
